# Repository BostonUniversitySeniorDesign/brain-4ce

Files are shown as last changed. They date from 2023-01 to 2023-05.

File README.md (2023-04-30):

<div style="text-align: center;">

# **Brain-4ce** - An EEG-based Brain-Computer Interface

</div>

<p align="center">
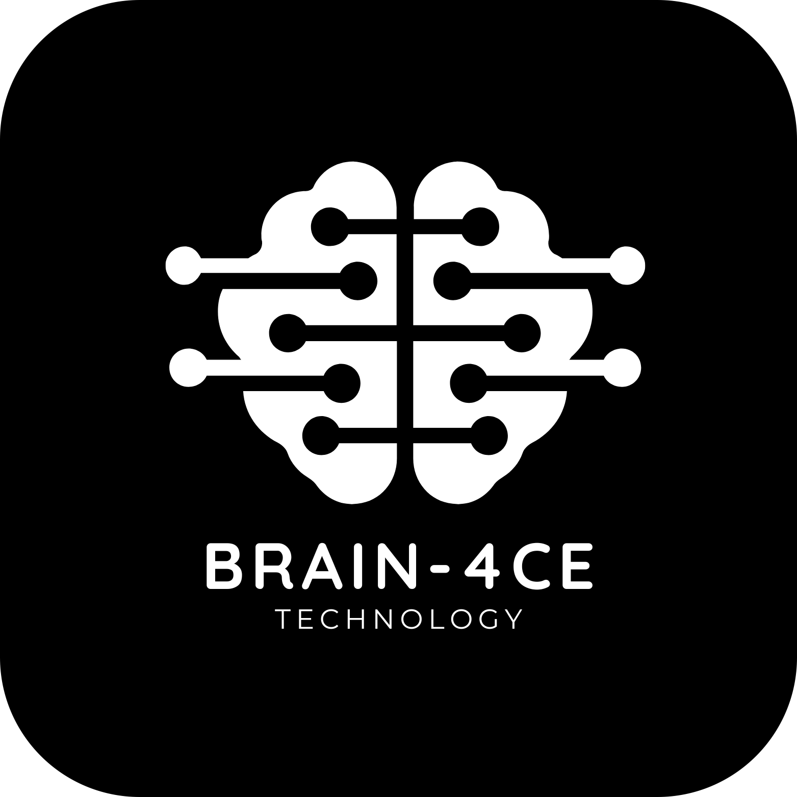
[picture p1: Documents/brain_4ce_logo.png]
Brain 4ce Logo
    
    <br>
    <em>Where thoughts become motion.</em>
</p>
<h2 style="text-decoration: underline; text-align: center">Designed by BU ECE 2023 Senior Design Capstone Team 4</h2>
<p align="center">
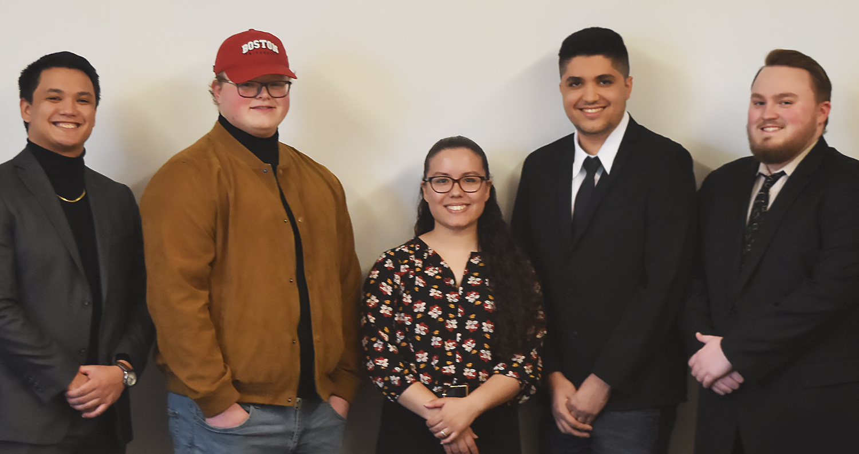
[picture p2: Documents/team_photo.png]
    
    <br>
    <em>From left to right: Brendan Shortall, Mitchell Gilmore, Dayanna De La Torres, Jonathan Mikalov, Alexander Johnson</em>
</p>
<br>

# Table of Contents
- [**Brain-4ce** - An EEG-based Brain-Computer Interface](#brain-4ce---an-eeg-based-brain-computer-interface)
- [Table of Contents](#table-of-contents)
- [Abstract](#abstract)
- [Getting Started](#getting-started)
- [Current State of the Project](#current-state-of-the-project)
- [Lessons Learned](#lessons-learned)
- [Bug Fixes](#bug-fixes)

<br>

# Abstract
The ability to manipulate objects using only your mind is no longer a far-fetched idea. While It may sound like something out of science fiction, our team has turned this into a reality. We have created a headset that utilizes electroencephalogram (EEG) technology to quickly and accurately record a user's neural activity. Our state-of-the-art deep learning algorithm then decodes these signals into predefined motor-imagery tasks.

This breakthrough technology is integrated with a computer game that provides the user with an environment to navigate using their mind. With the Brain-4ce (pronounced "Brain Force") headset, users can perform four different actions: rotating clockwise, rotating counterclockwise, moving forward, and moving backward. Each action corresponds to a physical motion that the user imagines themselves doing.

Our team was inspired to develop this project by our aspiration to bridge the digital divide for those who are physically disabled. With the Brain-4ce headset, users will be able to operate a computer, a wheelchair, and virtually anything else using nothing but their thoughts! The possibilities are endless, and we are excited to see what the future holds.
<br></br>

# Getting Started
- Please refer to our [Hardware Setup Guide](./hardware/README_HARDWARE.md) for instructions on setting up the hardware.
- Please refer to our [Software Setup Guide](./Virtual%20Environment/README_SOFTWARE.md) for instructions on setting up the software.
<br></br>

# Current State of the Project
As it currently stands, our project has three major components:
1. A working [EEG data capture headset](./hardware/electrical/cyton%20wired/) that interfaces with a [Python application](./GUI/) to monitor and record brain activity in real time.
2. A [convolutional neural network machine learning algorithm](./Physionet%20Dataloader/), trained on the recorded brain activity, for classifying motor-imagery tasks observed from a user wearing the headset.
3. [2D](./2D%20Game/) and [3D](./Virtual%20Environment/) video games developed in Python to demonstrate the efficacy of the neural network's brain activity classification.

The software communicates in real time using socket programming techniques to achieve parallelism and multithreading.
<br></br>

# Lessons Learned
- Developing on Apple Silicon, and ARM-based processors in general, is tricky for this project. Certain libraries, such as the [ChipKIT Core library](https://chipkit.net/wiki/index.php?title=ChipKIT_core) for compiling firmware onto the microcontroller, lack proper support for ARM architecture. We recommend performing all software development on an x64-based Windows machine. Some development is possible on Intel-based macOS and Linux, but it will probably save you a lot of headache to stick to Windows if possible.
- The microcontroller appears to have USB functionality built-in, which might make the USB to UART conversion unnecessary. This may be something to examine in [the documentation](https://ww1.microchip.com/downloads/en/DeviceDoc/PIC32MX1XX2XX%20283644-PIN_Datasheet_DS60001168L.pdf) during a future continuation of this project.
- The ADS1299 chip from Texas Instruments remains [difficult to obtain](https://www.findchips.com/search/ADS1299) as of Q2 2023 due to the ongoing chip shortage. We tried using the ADS1296 chip in its place, but this was unsuccessful because of differing startup and common-mode rejection configurations between the chips.
- If future boards are manufactured, it may be worth considering [paying for them to be machine-assembled](https://jlcpcb.com/parts). Assembling the boards by hand takes a long time and requires a substantial amount of electrical rules checking to ensure no shorts or incontinuity between components.
- Obtaining good skin contact for all electrodes is crucial to ensure proper reading of brain activity.
- The [OpenBCI Forum](https://openbci.com/forum/index.php?p=/discussions) is a great place to turn to for help troubleshooting. As is [their documentation](https://docs.openbci.com).
<br></br>

# Bug Fixes
- [Incorrect start byte configuration](https://github.com/atjohnson/brain-4ce-old/issues/10) - fixes an issue where the data stream is incorrectly formatted because the obsolete RFduino did some packet changing which no longer happens due to our wired USB connection.
- [Enable OpenBCI GUI to work with USB to UART controller](https://github.com/atjohnson/brain-4ce-old/issues/11) - fixes an issue where OpenBCI's GUI is unable to detect the Cyton board due to an ID mismatch with the USB to UART bridge IC.
- [Set up chipKIT Core library to work on local machine](https://github.com/atjohnson/brain-4ce-old/issues/12) - fixes an issue where Arduino IDE is unable to compile the firmware because it cannot locate the PIC32 compiler applications.
- [RXT and TXT LEDs not flashing](https://github.com/BostonUniversitySeniorDesign/brain-4ce/issues/4) - fixes an issue where the RXT and TXT LEDs on the board indicating data transmission over UART do not flash because the USB to UART bridge's firmware is configured improperly.

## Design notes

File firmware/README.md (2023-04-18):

# Firmware Configuration

OpenBCI really does not want their design to be used with a wired connection. From forum posts it is clear that their main motivation for this is safety, as a battery connection has a finite charge and a smaller discharge rate making the results of a potential hardware malfunction less dangerous. Unfortunately, the way they designed this required functionality of less popular hardware in order to transmit data, which ultimately fell into deprication. In order to make a design that is more robust to time, our team opted for a wired hardware connection. This means bypassing safe gaurds put into place that make implementation of a wired connection not possible by default.

In order to upload custom firmware to a fresh PIC32 microcontroller, the [bootloader](./UDB32-MX2-DIP.hex) must first be flashed using [MPLAB IPE](https://www.microchip.com/en-us/tools-resources/production/mplab-integrated-programming-environment) and a [PICkit 3 In-Circuit Debugger](https://www.microchip.com/en-us/development-tool/PG164130) as shown in [this video](https://youtu.be/z6AyIfWDiiU).

In terms of firmware the largest difference is the datapacket transformation done betweem the openbci cyton and the dongle. The start bit from the cyton is transmitted as `'A'` which is then converted to `0xA0` in order to be within their datapacket spec found [here](https://docs.openbci.com/Cyton/CytonDataFormat/#binary-format). In order to rectify this we edited the macro `OPENBCI_BOP` found in [OpenBCI_32bit_Library_Definitions.h](https://github.com/OpenBCI/OpenBCI_Cyton_Library/blob/master/OpenBCI_32bit_Library_Definitions.h#L19) from `'A'` to `0xA0` and made a [patch](packet.patch) in order to bypass this restriction.

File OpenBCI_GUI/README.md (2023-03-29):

# Configuring OpenBCI GUI

Since the OpenBCI GUI determines whether or not a devices is a Cyton by inspecting the vendor information on the USB controller, any device that was made with a different controller will by default not be found. To rectify this we made a patch to the OpenBCI GUI that removed the check for vendor specific indentification on the USB controller. In order to use this changes first set up an envirnment to compile the OpenBCI GUI. Details on how to do this can be found in their [wiki](https://github.com/OpenBCI/OpenBCI_GUI/wiki/Developer-Setup). After set up simply follow the commands below.

```bash
cd <This directory>
cp UART.patch <OpenBCI_GUI root directory>
cd <OpenBCI_GUI root directory>
git apply UART.patch
```

After making these changes if you follow the steps on the OpenBCI_GUI documentation to compile the project. Then the filtering that would prevent the custom design to be selectable.

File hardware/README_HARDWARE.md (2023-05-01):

# Hardware Setup
<div style="display:flex; justify-content:center;">
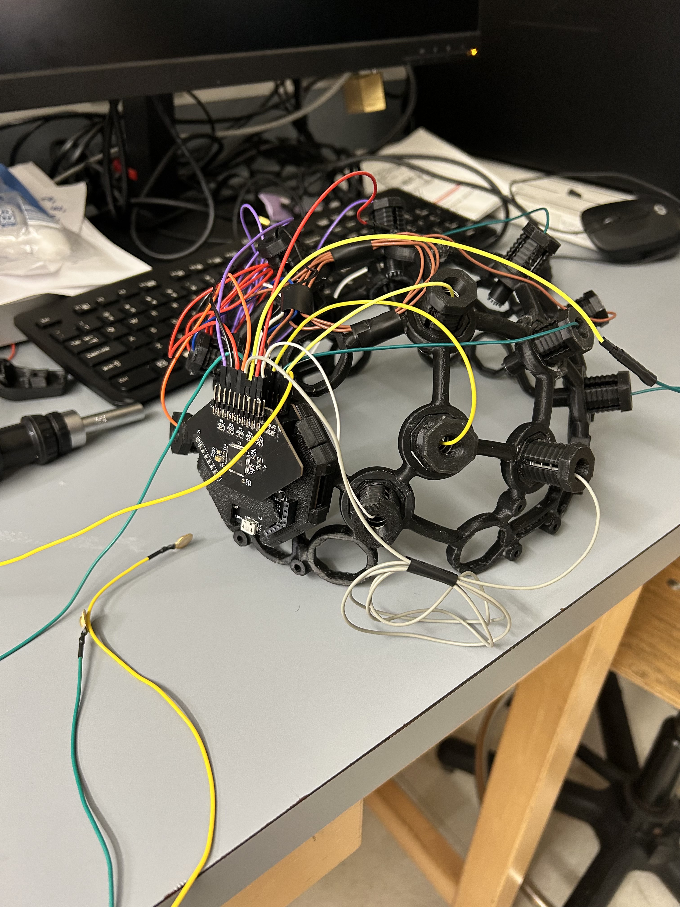
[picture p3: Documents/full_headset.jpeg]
Full Headset
  
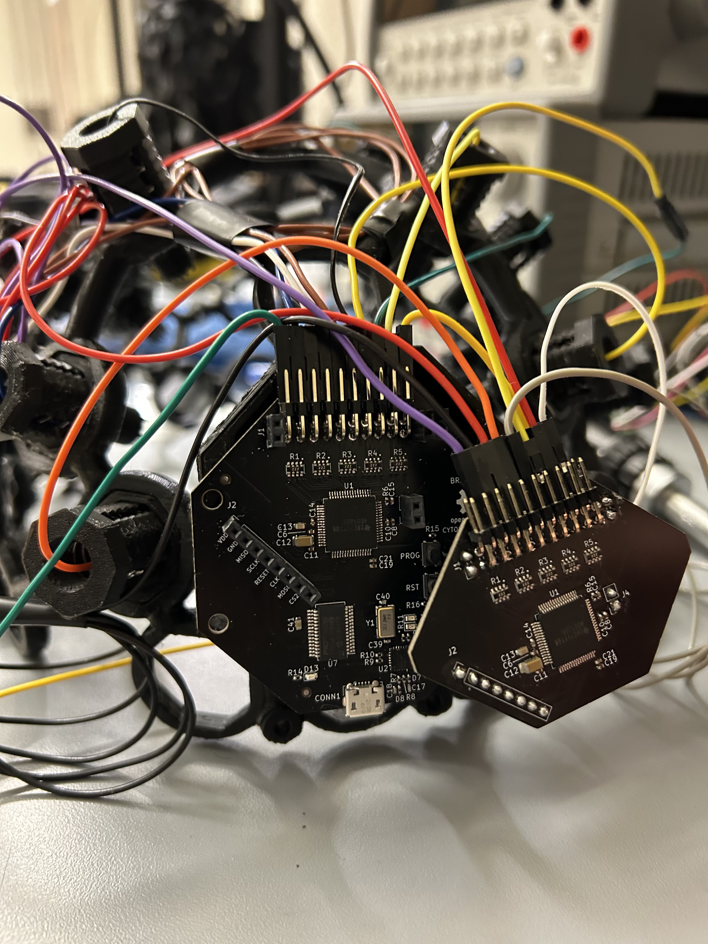
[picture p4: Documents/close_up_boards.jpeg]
Close Up of Boards
  
</div> 
<br>

The headset comes assembled out of the box with 16 electrodes placed in the rear of the headset body. The PCB is mounted in its casing on the back of the headset as well, with the probes attached to their correct pins.
1. Begin by attaching the included USB to the USB port that is visible on the Cyton board.
2. Plug the opposite end into any USB port on your PC. Ensure power is being sent to the board indicated by a blue LED on the top side of the Cyton. Once this LED is on, the hardware is ready to go.
3. If you would like to change the electrode positions, gently remove the probe by squeezing the sides of the outer electrode casing and pulling outwards. You should never change where the electrodes are connected to the boards, but if you choose to do so refer to the layout described in section 2.3.4 of the [User's Manual](../Documents/Team%204%20User's%20Manual.pdf).
4. Once you are ready to start the EEG system, connect an ear clip to each of your earlobes and place the headset on your head with the board on the back. Make sure that each of the probes is making contact with the scalp.
<div style="display:flex; justify-content:center;">
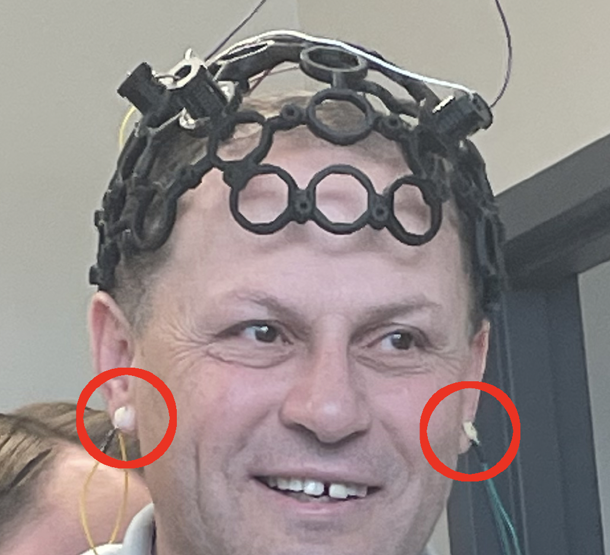
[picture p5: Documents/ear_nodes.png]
Ear Clips
  
</div> 
<br>

# Schematic/PCB/CAD Diagrams
- [Cyton Wired board schematic and PCB diagrams](./electrical/cyton%20wired/)
- [Cyton Daisy board schematic and PCB diagrams](./electrical/cyton%20daisy/)

# Bill of Materials
- [Cyton Wired BOM](./electrical/cyton%20wired/cyton%20wired%20bom.csv)
- [Cyton Daisy BOM](./electrical/cyton%20daisy/cyton%20daisy%20bom.csv)

# Significant Data Sheets
- [PIC32MX250F128B microcontroller](https://ww1.microchip.com/downloads/en/DeviceDoc/PIC32MX1XX2XX%20283644-PIN_Datasheet_DS60001168L.pdf)
- [ADS1299IPAG analog front end](https://www.ti.com/lit/ds/symlink/ads1299.pdf?HQS=dis-dk-null-digikeymode-dsf-pf-null-wwe&ts=1682901373303&ref_url=https%253A%252F%252Fwww.ti.com%252Fgeneral%252Fdocs%252Fsuppproductinfo.tsp%253FdistId%253D10%2526gotoUrl%253Dhttps%253A%252F%252Fwww.ti.com%252Flit%252Fgpn%252Fads1299)

# Power Requirements
- Micro USB to USB A power and data cable

# Vendor Information
- PCBs manufactured by [JLCPCB](https://jlcpcb.com)
- PCB surface mount components purchased from [Digi-Key](https://www.digikey.com)
- Headset components obtained from [OpenBCI](https://docs.openbci.com/AddOns/Headwear/MarkIV/?_gl=1*1e99fsi*_ga*NzI1MjAxMTkyLjE2ODI1MjkzNDM.*_ga_HVMLC0ZWWS*MTY4MjkwMDUzNC4zLjEuMTY4MjkwMDU0Ny40Ny4wLjA.)
- ADS1299 chips purchased from [AliExpress](https://www.aliexpress.us)
- PICKit 3 hardware debugger purchased from [Amazon](https://www.amazon.com)
- USB isolator purchased from [Adafruit](https://www.adafruit.com/product/2107)

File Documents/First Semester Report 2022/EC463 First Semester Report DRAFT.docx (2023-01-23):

# Boston University

# Electrical & Computer Engineering

# EC463 Senior Design Project

# First Semester Report

Submitted to

Prof. Alan Pisano

apisano@bu.edul

by

Team 04

Brain 4ce

Team Members

Alexander Johnson atjohnso@bu.edu

Brendan Shortall shortall@bu.edu

Dayanna De La Torres dayannat@bu.edu

Jonathan Mikalov jmikalov@bu.edu

Mitchell Gilmore mgilm0re@bu.edu

Submitted: 12/11/2022

#### Table of Contents

Executive Summary ii

1.0 Introduction 1

2.0 Concept Development 2

3.0 System Description 3

4.0 First Semester Progress 4

5.0 Technical Plan 5

6.0 Budget Estimate 6

7.0 Attachments 7

7.1 Appendix 1 – Engineering Requirements 7

7.2 Appendix 2 – Gantt Chart 8

7.3 Appendix 3 – Other Appendices 9

(right click on Table of Contents to update fields and page numbers automatically)

# Executive Summary - Alex

EEG-based Brain-Computer Interface

Team 04 – Brain 4ce

Individuals with physical disabilities, who struggle to operate a computer, need a noninvasive, but intuitive method of interfacing with the machine without musculoskeletal movement. We propose a wearable brain-computer interface (BCI) system to resolve this problem. Our BCI will consist of a 3D printed headset housing electrodes, a sampling board to obtain electroencephalogram (EEG) data from the electrodes, a machine learning model to classify the data into directional commands, and a 3D virtual environment to demonstrate functionality. We have designed an innovative approach to combine together the classification of neuronal action potentials (APs) with a 3D computer simulation.

(This should be written for management/public dissemination.

This will be published and distributed to ECE faculty.)

# 1.0 Introduction - Brendan

Since the turn of the century, brain-computer interfaces have grown in popularity. The number of publications surrounding this topic have nearly doubled since 2014 [1]. (https://www.frontiersin.org/articles/10.3389/fnsys.2021.578875/full) In many cases, invasive BCI technologies, which communicate with the brain via medical implant without interference from the scalp, have been shown to improve the lives of people with neurological illnesses [2]. (https://www.sciencedirect.com/science/article/pii/S0006349512033401?via%3Dihub) With this in mind, it is clear that the technology behind reading neural activity using medical implants has great potential.

However, invasive technologies may come with a slew of disastrous consequences for the user’s brain. A well documented complication of implanted neural electrodes are microglia immune responses. Microglial Cells release neurotoxins in response to pathological stimuli; neural implants have shown to amplify this response, causing major injury [3]. (https://www.sciencedirect.com/science/article/pii/S0165027005002931?via%3Dihub)

Invasive technologies for reading brain activity are also becoming increasingly more expensive. It is predicted that invasive BCIs will experience the fastest compound annual growth compared to non-invasive and semi-invasive techniques [4]. (https://www.grandviewresearch.com/industry-analysis/brain-computer-interfaces-market) The invasive approaches also include marginally higher expenses due to its physical implementation as well as required periodic medical check-ups [5]. (https://www.ncbi.nlm.nih.gov/pmc/articles/PMC3497935/) As a result, accessibility to invasive BCIs will become increasingly difficult for patients.

Our proposed solution avoids the dangerous risk of complications associated with electrode implants by implementing a safe and cost-effective method of non-invasive EEG pattern reading. As non-invasive EEG brain pattern recognition techniques improve, we hope to remove the risks associated with invasive techniques while maintaining and potentially improving the functionality of BCIs.

This project focuses on one of many potential applications of BCIs. In our use case, we hope to improve the usability of computer systems for physically disabled users, in a low-cost, low-risk way. To accomplish this, we will create a headset containing an array of EEG sensors positioned precisely around the user’s scalp. These sensors will be read by a mounted printed circuit board (PCB) that will communicate directly with a computer. As real time data is received on the computer, our machine learning algorithm will constantly analyze the data and make a prediction on the user’s intended movement. This prediction will be sent to our virtual environment, where a user-controlled object will move based on the user's intended action. This virtual environment acts as visual feedback for the user, so that they can adjust their behavior for the results they desire. This closed loop system will demonstrate the capabilities of non-invasive neural monitoring techniques, and will lay a foundation for future research involving non-invasive EEG based BCIs.

# 2.0 Concept Development - Jonathan

Here you describe your analysis of the customer’s problem and its translation into specific engineering terms. You should address:

- your engineering understanding of the customer’s problem,
- the conceptual approach you have chosen to solve the problem, and

You must reduce the customer’s needs to a small number of engineering requirements. You must identify those requirements as a 1-page attachment, Appendix 1

Elaborate on the conceptual approach for your project. Explain briefly why you chose your proposed concept, and mention one or two of the alternative solutions you considered and abandoned.

(This section should be 2-3 pages)

You MUST include a 1 page Requirements list as Appendix 1.

To address the complex challenges that neurologically and physically disabled individuals face when operating a computer, our team was immediately faced with many dilemmas regarding actual implementation. First, it was made clear that the machine learning algorithm needs to communicate with both the signal processing unit and the virtual environment efficiently. Accounting for this, we considered a variety of neural network algorithms that might work optimally given our outlying data sampling techniques as well as limited CPU memory usage. These were including but not limited to: Deep Recurrent Neural Networks (DRNNs), Hidden Markov techniques, as well as the Bidirectional Long-Term Short Memory Neural Network (LSTM). After careful review of the benefits of each deep learning method, it was concluded that the LSTM model would be the best fit for our data classification model given its lack of over-reaching memory usage as well as its consistent learning ability to classify motor imagery tasks. Classifying motor imagery tasks is very important for overlying project concept as they deal directly with the backbone of an EEG-based brain computer interface. As such, we anticipate that our model needs to classify data accurately for it to be optimally used by a disabled individual.

Another core tenet behind a brain-computer interface is its ability to be worn with comfort and ease-of-access. Thus, it must not cause too much pressure to the forehead of the individual and must not be congested with wires across their desk or table. Understanding that some disabled individuals may tend to feel more sensitive pressure to the head, our team has agreed upon a thorough weight requirement of no more than 1 kilogram. This includes the headset in its entirety as well as all its connected cables to the Arduino Uno and CPU. To account for the lightweight requirement, we implemented an OpenBCI© 3D print design that allowed us to construct a headset ¼ of our weight requirement (excluding all required cables).

Our hardware requirements, which were initially relatively straightforward to design, ended up being presented with creative challenges. In one specific example, the printed circuit board’s Bluetooth module (important as it serves a direct link between the MCU and CPU), was no longer being sold in stores and had become essentially defunct. As a result, our team had to develop a new set of engineering requirements that maintained our design’s level of efficiency while also establishing an efficient method to connect a circuit board to a CPU. As a result, we developed an Arduino Uno component for the underlying architecture that will serve an important role in transferring real-time signal processing data into our CPU, to be received by the machine learning algorithm. This component of our project also needs to be optimally efficient, in such a way that it can at least process up to 500 samples of alpha & beta brainwave data per millisecond. For the detection of specific motor imagery tasks present within an EEG, our team discovered a variety of data features that can be used to relatively classify the thought being present. As a particular example, the P300 wave, which is commonly used by lie-detectors as well as other BCIs, can be seen in an EEG as a physiological pattern being produced by the thought of a particular reaction (ie. decision making).

The virtual environment component of the project, while primarily serving as a proof-of-concept for the core brain-computer interface, serves an integral role in displaying the role of BCIs used in everyday life. As such, the environment itself was designed to be graphically oriented to be appealing to a wide array of users, and present only simple features. If anything more be present, epilepsy patients or others with visual sensitivity will not be able to use this component to their advantage. An important engineering requirement regarding the use of the virtual environment is its frame rate, graphics support, and its ability to process machine learning classification in real-time. The reason of its importance mostly stems from the ability that disabled individuals need to be able to operate in a timely manner so as to not inconvenience them compared to other products on the market. As such, we discovered that the graphics library used for our 3D environment (Panda3D) not only supports an adequate framerate (usually up to 60 frames per second) but also supports a wide array of graphics cards, ranging from various versions of NVIDIA to Intel.

# 3.0 System Description - Alex

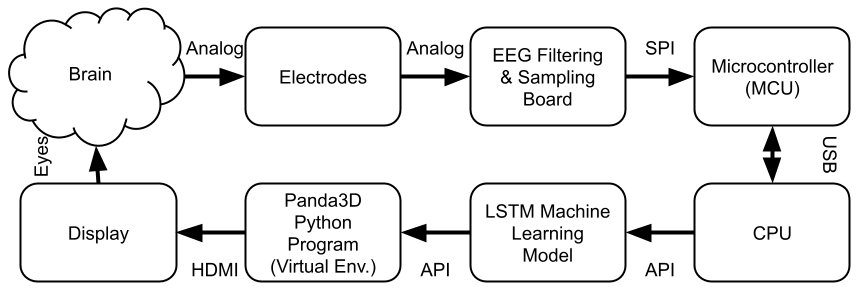
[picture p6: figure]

Figure 1. Block diagram of the system.

Our system begins with a set of reusable dry EEG electrodes housed in OpenBCI’s Ultracortex Mark IV headset, 3D printed using PLA material. These electrodes, located on the user’s scalp following the international 10–20 system configuration, read analog motor-imagery electrical signals in real time from the user’s brain and pass those signals along wires to OpenBCI’s Cyton PCB. Those analog signals are then filtered, digitally sampled, and passed along the PCB in 8 channels to the microcontroller. The microcontroller processes the digital signal into usable data for transmission over USB.

After the data is transmitted over USB, the computer decodes the input using the OpenBCI software suite, and it is then fed through our long-short term memory (LSTM) artificial neural network by a custom designed API. The LSTM model then classifies the data into 4 classes each representing different directions: left, right, up and down. This new dataset is interpreted by another custom API to generate the corresponding object movement in our virtual environment Python application. The final visual output of our virtual environment is displayed on a computer monitor using an HDMI connection. The user then sees this movement on the computer screen and can adjust their motor-imagery task thought patterns accordingly.

The user interface is a three-dimensional virtual environment generated in Python using Panda3D libraries. It consists of an object, tentatively a sphere, suspended on a flat surface in the environment. A set of obstacles move towards the sphere, and the user is tasked with moving the sphere out of the way before it collides with the obstacle. This game design is how our proof of concept is demonstrated.

Here you describe in technical detail WHAT YOU WILL PROVIDE as a solution. It should be as detailed, specific, quantitative, and engineering-oriented as possible.

Avoid grand promises and vague descriptions. Ruthlessly edit collective, vague adjectives and claims (e.g. “We will have high power and long life in our nuclear transmitter”). Follow the concept you are recommending from section 2.

You MUST include a system block diagram (approximately a level 2 functional decomposition) for your system/software, including a brief narrative explanation. The system block diagram should identify clearly the major subsystem blocks. Directed arrows should represent data or control flows. It is appropriate to use a full page for the system block diagram, and to import a figure developed in another application, e.g. Visio.) The following was done in Word Draw.

Figure 2. Block diagram of the Beam Transporter.

If appropriate, include a discussion of the user interface with your preliminary GUI. You can sketch the project or include a photo of your mockup.

If it is a software project, you should include high-level pseudocode of how the project will operate.

(This section should be 2-3 pages. It is an overview description.)

# 4.0 First Semester Progress - Dayanna

4.0.1 Hardware Progress

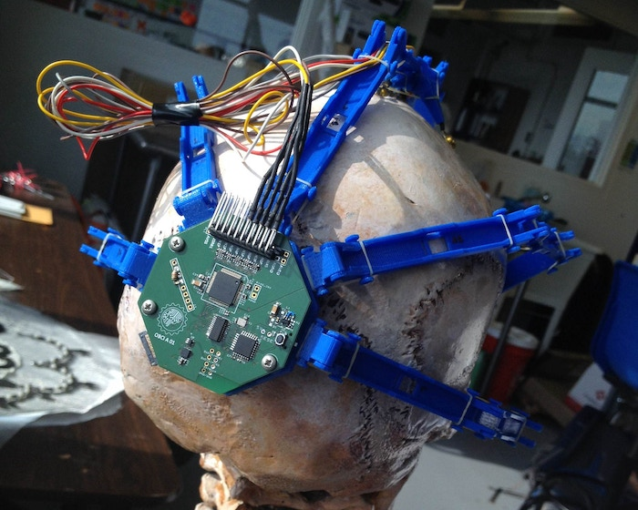
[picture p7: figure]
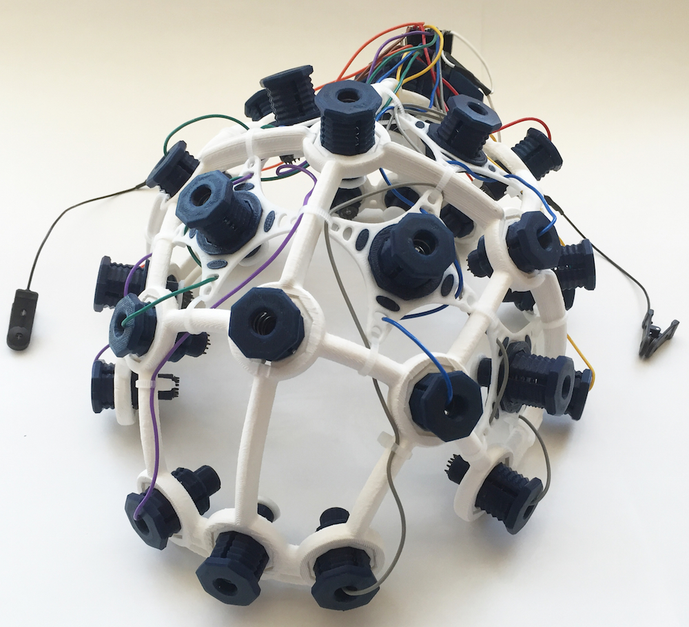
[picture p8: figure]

Figure 2a Figure 2b

Figure 2: The headset Design. Figure 2a depicts the original design. Figure 2b depicts the new updated design.

4.0.1.1 Headset Design and Fabrication

We based our headset on open source designs we were able to find. After 3D-printing the first iteration (figure 2a), it was promptly discarded due to structural integrity concerns. Specifically, the fact that it was held together with orthodontic elastics. We have now moved onto the second iteration of the headset (figure 2b) which we deem to be more structurally intact and solid. Moreover, it has better assigned locations for the electrodes. Together, this makes the design not only structurally better but also more comfortable for the user.

4.0.1.2 Circuit Board Design and Fabrication

We are modeling our circuit board after the OpenBCI sampling board. Due too the cost of the board being around $1000, we are creating it in-house. This semester we printed the PCB, ordered the necessary components, and are beginning the process of soldering said components onto the board. We have run into one component issue which is with the Bluetooth/RF module. The module used on the original OpenBCI board has been discontinued and is no longer on the market. Handling this situation and researching alternatives was a top priority for this semester in order to finish the board and begin collecting data samples.

4.0.1.3 Collecting EEG data

This semester we created our first prototype of the EEG system where our goal was just to receive some electrical output from the system (no emphasis on collection yet). To obtain proper readings from the EEG electrodes, we had to amplify our voltage output by 900x. To amplify the voltage output, we created a differential amplifier circuit using a set of resistors, a 5V power supply, and an MCP6002 operational amplifier. As an additional setup, electrode wires were connected to the voltage output of the circuit in order to obtain a potential physiological response from a test subject. In order to test the performance of the EEG electrodes, we attached them to multiple test subjects’ arm using conductive paste. Additionally, we detached them from the arm and placed them directly on the forehead to examine a potential change in results. Ultimately, we were unable to obtain readings from the EEG electrodes. The oscilloscope displayed a constant zero voltage regardless of the electrode placement on our test subjects. Moving forward, the electric circuit needs to be changed to address these issues.

As a side attempt to collect data, research was done into Arduino-based EEGs. While it may not be as precise, we are hoping that it will provide usable data that can then be used to train the LSTM neural network. The parts have been ordered and we have begun 3D printing the necessary components to create this smaller system.

4.0.2 Software Progress

4.0.2.1 Machine Learning Model

We have begun working on an LSTM algorithm; however, it has not yet been trained nor tested on our data due to the inability to successfully collect any to this point. The purpose of working on one thus far has been to familiarize ourselves with inputting and reformatting data into LSTMs, working with LSTM neural networks

To this date, the LSTM neural network has been trained and tested on online public databases containing EEG data. In some cases, this has failed due to a lack of understanding of the data. Machine learning algorithms are sensitive to matrix dimensions and being unfamiliar with them, and what each row/column may signify poses a problem. The NN has worked on some EEG data, namely if it is picking up readings of physical activity. This however, is different from trying to pick up thoughts which is our ultimate goal.

The most successful tests run thus far have been on physical motion. Specifically, the data that uses an accelerometer or some other type of sensor readings to measure motion/ type of motion. This has worked with over 90% success.

4.0.2.2 Virtual Environment

This semester we have started setting up Blender for our final virtual environment. The first task completed was running Panda3D, a game engine used to render 3D environments/games, to test for graphic issues and framerate compatibility. We did this by running sample files provided by the library and measured a variety of statistics (FPS, refresh rate, render distance) and compared them on different operating systems, specifically Windows and MacOS.

We created a draft Blender virtual environment for the initial prototyping and construction of the virtual game. This was followed up by interfacing Blender models with a Panda3D script, as this will be used to control the game in real time.

This section is a detailed summary of the progress your team has made this semester. Include key results from your First Deliverable Testing.

# 5.0 Technical Plan - Mitchell

The first stage in completing our solution is EEG assembly. We have components ordered and currently in shipping but following the arrival we will have the following parallel tasks.

- Task 1: Assemble EEG PCB
  - Description:

The EEG PCB shall be assembled using already purchased components. It shall be assembled in accordance with the Schematic and Layout save for a few divergent cases documented in the logbooks. Additionally This will entail writing the provided firmware from OpenBCI to the onboard microcontroller.

  - Lead: Mitchell
  - Support: Brendan
- Task 2: Assemble EEG Headset
  - Description:

The EEG headset shall be assembled in accordance with the assembly instructions provided by OpenBCI in the UltraCortex repository (https://github.com/OpenBCI/Ultracortex/tree/master/Mark_III_Nova).

  - Lead: Brendan
  - Support: Mitchell

Following completion of these tasks we will begin our second stage focused on data collection to train the machine learning model.

- Task 1: Collect Data from EEG
  - Description:

Data shall be collected from our prototype EEG for ML training purposes using OpenBCI GUI. The data collection process will be automated by an instructional video that will guide a user through different visualization and movement tasks to be classified.

  - Lead: Mitchell
  - Support: Brendan
- Task 2: Label EEG Data
  - Description:

Using the timing intervals of the guided video we shall assign labels to certain sections of the EEG so the ML algorithm can be trained in a supervised manner.

  - Lead: Brendan
  - Support: Mitchell
- Task 3: Forward Data to ML Lead
  - Description:

Following labeling the dataset will be released to the ML lead to begin training the ML algorithm on modality specific data.

  - Lead: Mitchell
  - Support: Brendan

After data collection we will begin the EEG redesign and ML design, train, and test phases as well as complete the virtual environment.

- Task 1: Schematic Redesign
  - Description:

The original design for the PCB is inherited from a previous open source project that is no longer maintained. In its base state it does not meet our needs, so we shall redesign it to transition from obsolete wireless communications to usb for sending data to the computer, while doubling the number of probes and removing unwanted components.

  - Lead: Mitchell
  - Support: Brendan
- Task 2: EEG Layout
  - Description:

Following the schematic redesign to include all the features we need. We shall layout a PCB in accordance with the new schematic so our new electrical system can be fabricated.

  - Lead: Mitchell
  - Support: Brendan
- Task 3: Design and Train ML Algorithm
  - Description:

Following the creation and labeling of data we shall begin work creating a LSTM Neural Network that will be trained to classify the different observable action potentials (AP) in the brain corresponding to different premotion thoughts.

  - Lead: Dayanna
  - Support: Brendan, Mitchell
- Task 4: Test ML Algorithm
  - Description:

Following training and hyperparameter tuning a partition of the dataset not yet seen by our machine learning model will be used to quantify real world performance.

  - Lead: Dayanna
  - Support: Brendan, Mitchell
- Task 5: Develop Signal Processing Scheme
  - Description:

EEG signals are inherently very noisy so as to mitigate errors associated with noise, various processing techniques will be tested in an attempt to improve classification. These methods are but not limited to cepstral analysis, parametric signal modeling, Kalman filtering as well as other to be determined relevant methods of deconvolution and reconstruction.

  - Lead: Mitchell
  - Support: Brendan, Dayanna
- Task 6: Finalize Virtual Environment
  - Description:

In order to show visually our system functioning we need a virtual environment that has an object that can be controlled with user input. Eventually this user input will be replaced by the ML predictions, but in order to finalize the virtual environment separately from the rest of the project it shall initially be configured to take in a mouse and keyboard as input.

  - Lead: Jonathan
  - Support: Alex

Following completion of the redesign phase we will need to fabricate and assemble the new EEG PCB.

- Task 1: Fabricate PCB
  - Description:

After the PCB is layed out, it will need to be fabricated. Due to the stackup of the design, we will not be capable of fabricating the PCB at BU. Therefore, the design will need to be fabricated externally through a third party vendor.

  - Lead: Mitchell
  - Support: Brendan
- Task 2: Assemble PCB
  - Description:

Following PCB fabrication the boards shall be assembled to have all its components soldered to the board to achieve full functionality and so the on board microcontroller unit (MCU) can be programmed. We will explore options for external assembly to streamline the design or assembling internal at BU.

  - Lead: Mitchell
  - Support: Brendan

After having the redesigned EEG made physically it will be time to integrate all the separately developed components into a pipelined system.

- Task 1: Interface ML Algorithm with EEG in realtime
  - Description:

With the ML Algorithm and the EEG machine tested and verified as standalone units, the two shall then be integrated together into a pipelined system.

  - Lead: Dayanna, Alex
  - Support: Brendan, Mitchell
- Task 2: Interface between ML ALgorithm and Virtual environment in real time
  - Description:

With the ML algorithm and virtual environment tested and verified as standalone units, the two shall then be integrated together into a pipelined system.

  - Lead: Dayanna, Jonathan
  - Support: Alex

Following the completion of these tasks we will have a fully functional end-to-end system to read EEG pre-motion thoughts into observable computer actions.

Describe how you plan to complete your proposed solution.

The performance period of this plan is December 11, 2012 – May 1, 2013. You should not discuss tasks that are already completed or plans that are in the past! Remember the functional testing of your project is the week of April 1 (This is when the project is “due”)

Organize this section as a discussion of tasks and milestones, integrated with your professionally prepared Gantt Chart (Appendix 2)

Tasks should be clearly named. They should be described with a verb-an action word. They should have a clear, measurable deliverable product at their completion.

Task 2. Battery power supply

A 3V, 200 mA battery power supply shall be designed, fabricated and tested. It shall be rechargeable from an external connector and meet specifications for weight, battery life, and heat dissipation. The design should be tested with a dummy load of 900 ohms. Lead: Captain Kirk; Assisting: Scottie.

(No more than 4 pages.)

# 6.0 Budget Estimate - Brendan

Figure 3: The team’s current expenditures, and a summary of our remaining budget.

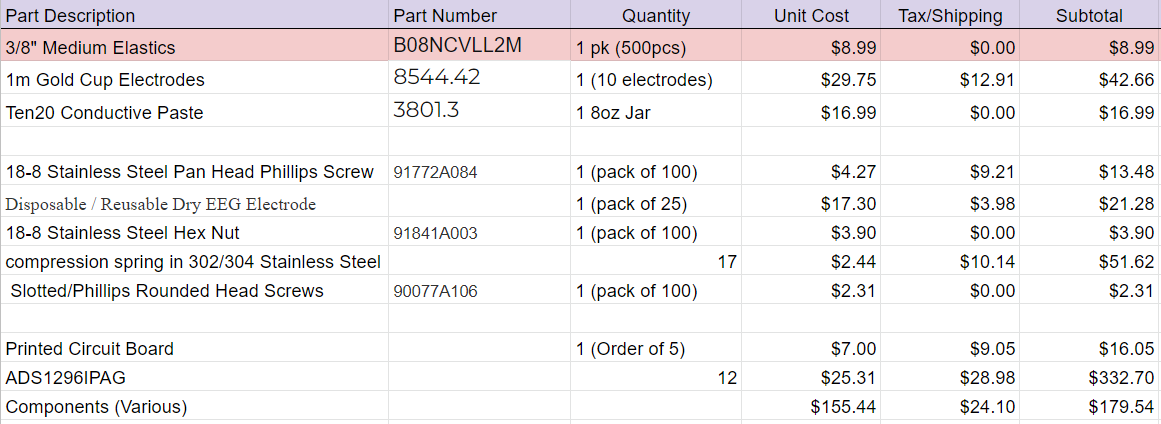
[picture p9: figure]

Our budget is limited to $1,000 from the Boston University ECE department. However, we have received additional funding from the Arrow Electronics Innovation Fund in the amount of $2,500. Our team plans to stay within the original $1,000 budget, but the additional funding gives us a safety cushion if need be.

With a large portion of our project being strictly software, our budget is almost exclusively used on hardware. This includes the physical headset itself, the EEG sensors, and the PCB. The first 8 items in our materials list refer to the headset. These items include electrodes, screws and bolts, springs and other various hardware needed to construct our 3D printed headset. The last three items involve the PCB and the necessary components. The part listed as “ADS1296IPAG” refers to a bio-sampling chip that will be integrated into the circuit board. The minimum quantity to order was 12. We needed only 4 or so total, but this part is essential to our project and there are no other viable alternatives. We decided buying 12 and spending the additional money is in the team’s best interest. Lastly, the item listed as various components refers to diodes, capacitors, resistors and whatever other small electronics we need for the circuit. A more detailed list of these components can be found in the appendix section 7.3.1.

In all, we have spent roughly ⅔ of our allocated budget. With that being said, essentially all of our necessary purchases have been made with no major foreseeable expenses . Financially, we are in a very comfortable position; However, we will continue to track our expenses and ensure that we remain within budget.

# 7.0 Attachments

# 7.1 Appendix 1 – Engineering Requirements

Team # Team Name:

Project Name:

Requirement | Value, range, tolerance, units
Headset circumference | <=
Power | 1GJ photon source, and 3V battery
Transport range | >100 light years
Transport nodes | 3 in simplex mode (no return possible); 2 in duplex mode (round trip stored)
Radiation dose | 20 REM/trip +1 REM, -3 REM
Transport error rate | < 10⁻¹¹ molecules of normal body mass < 10⁻¹⁵ molecules when sending DNA data

These are your requirements specifications that transform the customer’s needs and wants into specific engineering requirements. See the course textbook regarding the formation of appropriate specifications. Generally these are at the system integration level. Each unit that you design will have its own internal specifications, but these are usually not listed in a proposal.

Specifications should not include vague environmental constraints.

Specifications should not be statements of technology preferences or early design decisions (e.g. “The unit shall use Li ion batteries” is not a specification.)

Not more than one page.

# 7.2 Appendix 2 – Gantt Chart

Here you provide a STANDARD PRESENTATION OF THE TASKS, MANAGEMENT, AND SCHEDULE of your efforts. You can access MS Project to create a professional Gantt Chart and cut and paste the chart here. (This template was done MS Project and saved to Word. Remember: Clear date headers; dependencies; milestones; hierarchical tasks; course milestones.

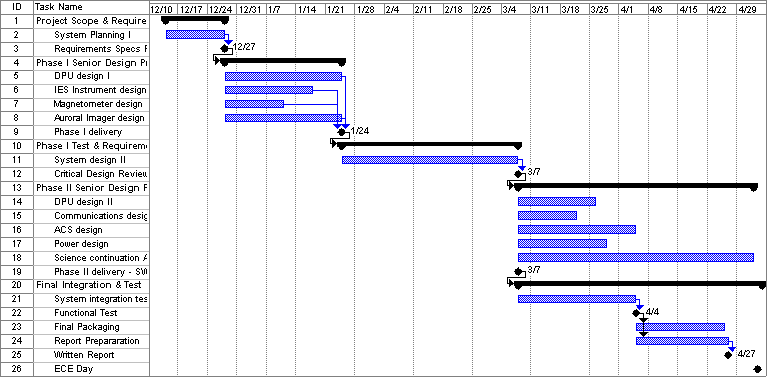
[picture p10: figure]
PjCopyPic

You need not include other MS Project columns like start and end dates, durations, support, etc. Make major milestones clear.

# 7.3 Appendix 3 – Other Appendices

Other typical attachments that are added to bolster the competitiveness of your proposal:

- Technical references (in proper bibliographic form) including key URLs.
- Your drawings and schematics (rather than embedding in text)
- Team information sheet (Biographical paragraph on each member; phone numbers and e-mail, history of team and company)

Do not pad with mundane data sheets and application notes.

7.3.1

A more detailed list of the individual components listed in Figure 2.

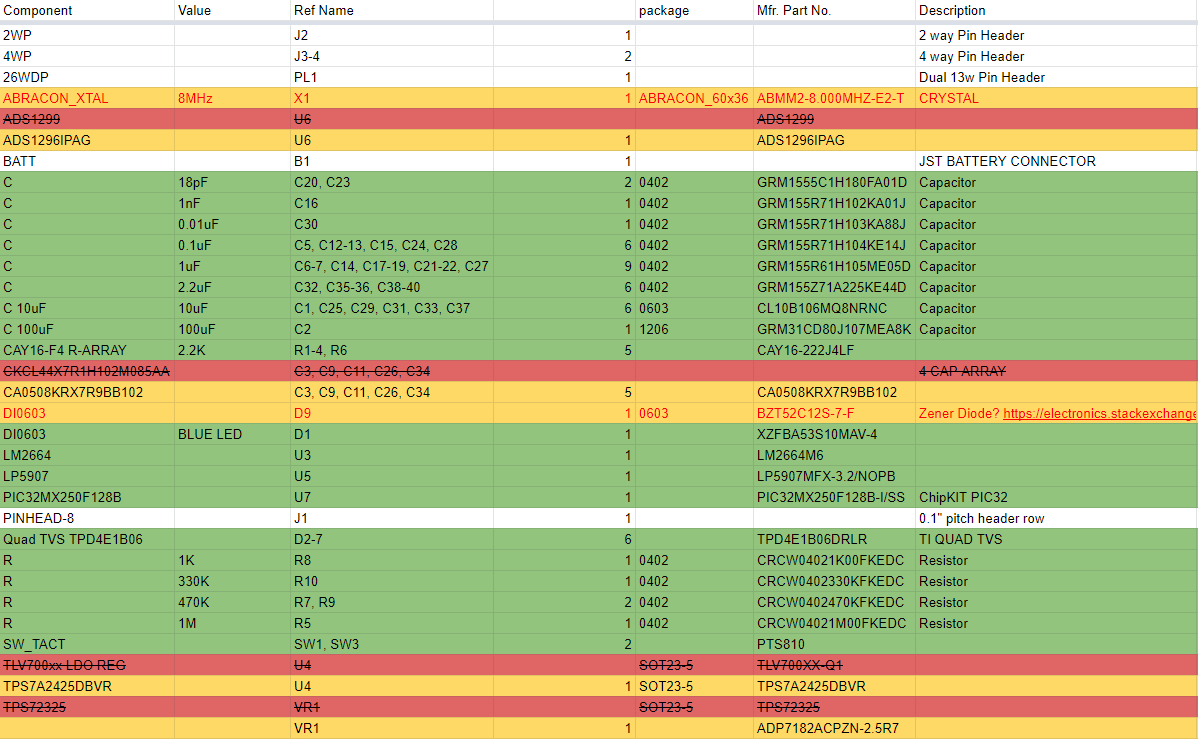
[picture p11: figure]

References:

[1] S. Saha et al., “Progress in Brain Computer Interface:

Challenges and Opportunities,” Frontiers in Systems

Neuroscience, vol. 15, Feb. 2021, doi:

10.3389/fnsys.2021.578875.

[2] L. R. Hochberg, “Intracortical Brain-Computer Interfaces for the

Restoration of Communication and Mobility,” Biophysical Journal,

vol. 104, no. 2, p. 376a, Jan. 2013, doi: 10.1016/j.bpj.2012.11.2094.

[3] V. S. Polikov, P. A. Tresco, and W. M. Reichert, “Response of

brain tissue to chronically implanted neural electrodes,” Journal of

Neuroscience Methods, vol. 148, no. 1, pp. 1–18, Oct. 2005, doi:

10.1016/j.jneumeth.2005.08.015.

[4] “Brain Computer Interface Market Size | Industry Report,

2027,” Available:www.grandviewresearch.com.

https://www.grandviewresearch.com/industry-analysis/brain-

computer-interfaces-market

[5] J. Shih, D. J. Krusienski, and J. R. Wolpaw, “Brain-

Computer Interfaces in Medicine,” Mayo Clinic Proceedings,

vol. 87, no. 3, pp. 268–279, Mar. 2012, doi:

Spell Check Everything!!!!

Paginate and edit footers and headers for your team.

Work through at least two drafts before submitting final document.

DO NOT bind, put in fancy covers or otherwise embellish. Simply clip with spring binder in upper left corner.

Use MS Word or PDF format for final document.

Submit one soft copy to course via Blackboard Digital Drop Box, and one copy to customer (include cover letter to customer).

The body of the proposal should not exceed 20 pages.

(This excludes the cover page, table of contents, executive summary, and attachments.)

Team X YourTeamName 11/15/16

Team X YourTeamName

EC 463 – BOSTON UNIVERSITY ELECTRICAL & COMPUTER ENGINEERING CAPSTONE SENIOR DESIGN PROJECT

Project Proposal page

Project Proposal

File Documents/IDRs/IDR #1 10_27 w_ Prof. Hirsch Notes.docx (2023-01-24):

- We need low noise instrumentation amplifiers
- Maybe directly solder parts on a PCB
- Breadboard is worth a try
- Compare price vs accuracy
- Avoid long traces and wires to improve performance (reduces noise)
- Vladimir Kleptsyn room 106 near senior design rooms for chips
- Maybe Dayanna can get wholesale stuff for us from CVS

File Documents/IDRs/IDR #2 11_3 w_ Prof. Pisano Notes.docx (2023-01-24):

- What can we show them in 2 weeks?
  - What can we put together that shows a viable test case
  - Shoot for hardware prototype
  - Signal generator and have it display it might be a viable first prototype
  - Likes the fact that we’ve looked at a lot of stuff
  - Thinks this is a great project and is very excited to see this come to fruition

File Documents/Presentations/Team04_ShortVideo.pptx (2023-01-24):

## Brain Force An EEG-Based Brain-Computer Interface

By Alexander Johnson, Brendan Shortall, Dayanna De La Torres, Jonathan Mikalov, Mitchell Gilmore
Client: Alan Pisano
Team 04

## Project Goal

To use a brain computer interface to aid disabled individuals in using a computer by reading neural activity related to thoughts of motion and translating these thoughts into distinct commands.

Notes: “Tweetable” summary of your project - 30 seconds or less

## System Requirements & Components

01

3D Printed Headset

- Comfortable, easily removable, dry EEG sensors.
- Lightweight, feasible to wear for long periods of time.
- Structural integrity will hold over multiple uses.

- Biosampling, Filters.
- 12+ Channels
- USB Connectivity

02

EEG Sampling Board

03

Machine Learning Model

- LSTM Neural Network
- 4+ classifiable states
- 60+% accuracy

04

Virtual 3D Environment

- Translate ML output into distinct actions.
- Small tasks for users to complete.
- Make a scoreboard for ECE day competition.

## Usability of Product

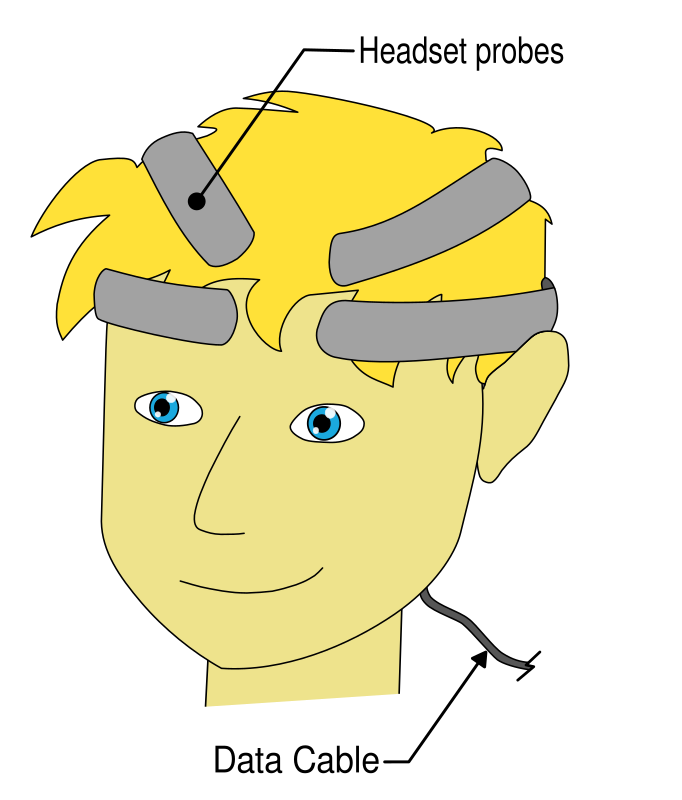
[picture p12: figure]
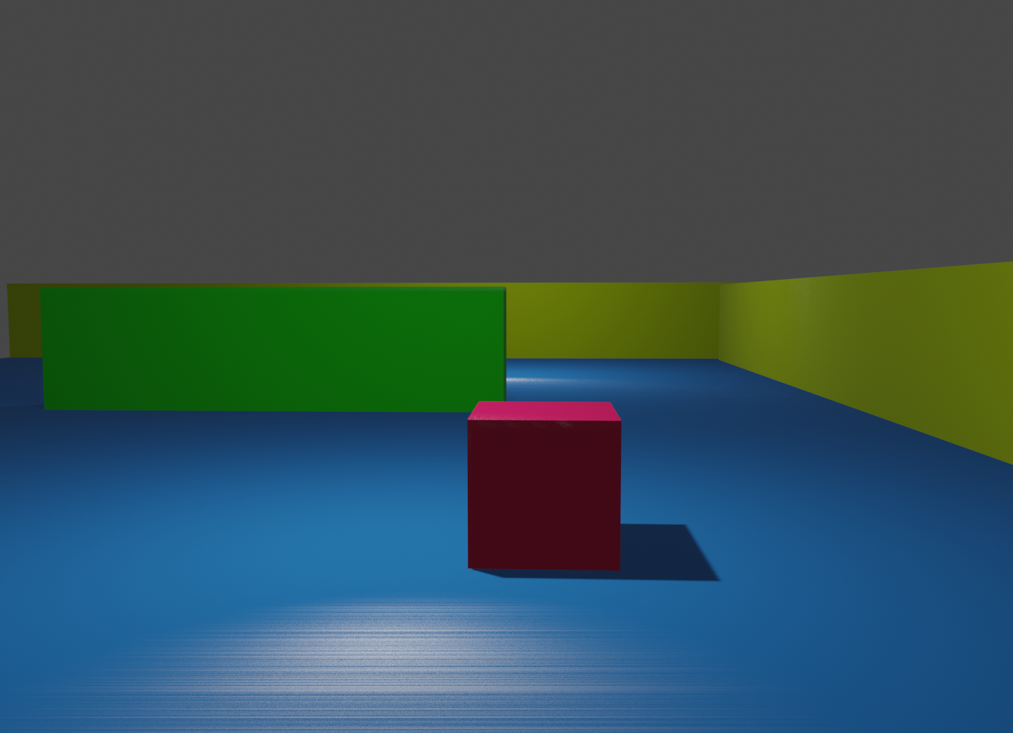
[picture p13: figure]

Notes: How would someone use your project? This is a non-technical, and functional overview of usability.

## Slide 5

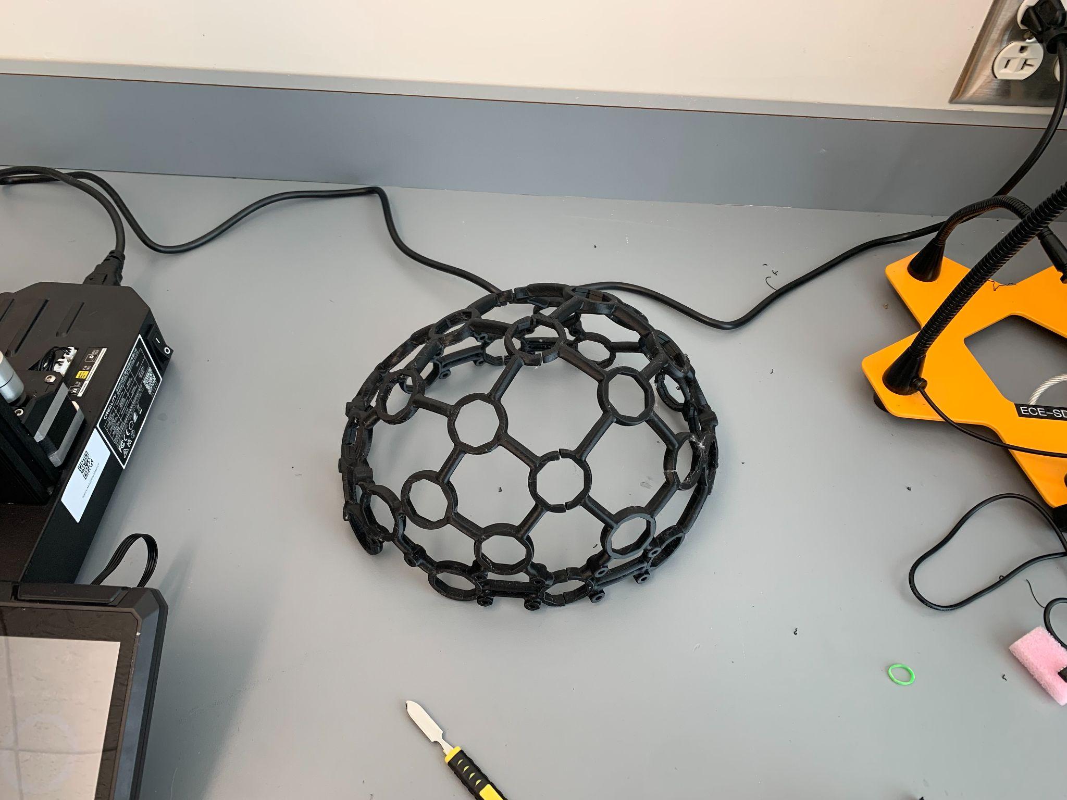
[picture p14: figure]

## Initial Prototype Test

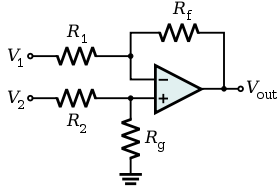
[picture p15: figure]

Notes: “Tweetable” summary of your project - 30 seconds or less

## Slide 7

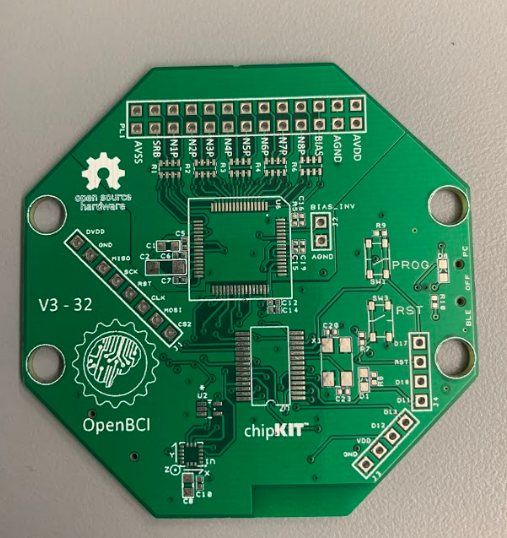
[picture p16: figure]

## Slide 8

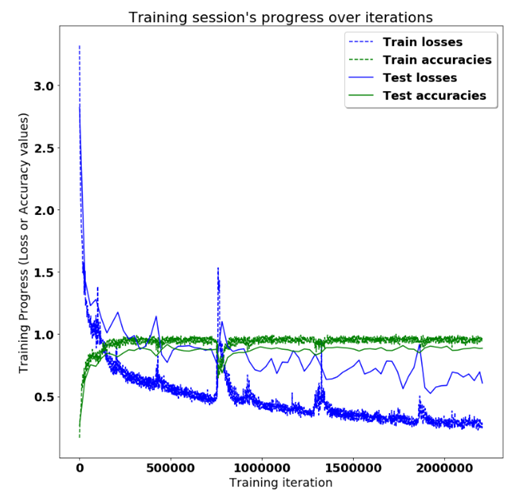
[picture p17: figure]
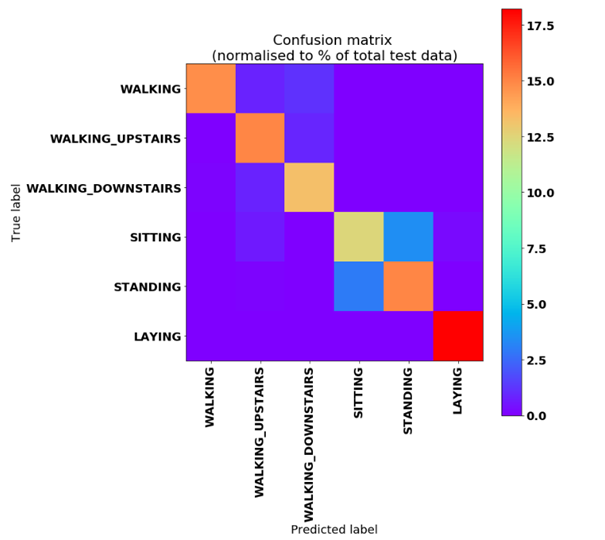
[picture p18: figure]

## Last Stage/ Working Product

Fully integrate the headset, neural network, and virtual environment to function seamlessly in real time.

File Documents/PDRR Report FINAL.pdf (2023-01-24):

EC 463 – BOSTON UNIVERSITY ELECTRICAL & COMPUTER ENGINEERING CAPSTONE SENIOR DESIGN PROJECT | 1

# Boston University Electrical & Computer Engineering

## EC463 Capstone Senior Design Project

# Problem Definition and Requirements Review

EEG-based Brain-Computer Interface

Submitted to:

Prof. Alan Pisano
apisano@bu.edu

by
Team 04
EEG-based BCI
Team Members:

Alexander Johnson atjohnso@bu.edu Brendan Shortall shortall@bu.edu Dayanna De La Torres dayannat@bu.edu Jonathan Mikalov jmikalov@bu.edu Mitchell Gilmore mgilm0re@bu.edu

### Submitted: 10/14/2022

## Customer Sign-Off _______________________________________

EC 463 – BOSTON UNIVERSITY ELECTRICAL & COMPUTER ENGINEERING CAPSTONE SENIOR DESIGN PROJECT | 2

# EEG-Based Controller for Navigating a Virtual 3D Space

### Alexander Johnson, Brendan Shortall, Dayanna De La Torres, Jonathan Mikalov, and Mitchell Gilmore, Team 04

Abstract—This project demonstrates the capabilities of non-invasive electroencephalograms (EEGs) in predicting an
intended movement of a user. A wearable headset containing an array of sensors relays neural information to a signal
processing unit, which transforms the raw input into data more suitable for further processing. From there, a trained machine learning algorithm determines a user’s intended action in a virtual 3D space. This grants the user three degrees of freedom. The intended actions will be displayed on a screen depicted as an object moving through a videogame-like three-dimensional space. This will provide feedback to the user and allow them to make adjustments. The user will be given a task to complete within the virtual environment to demonstrate the effectiveness of the device.

Index Terms—algorithm design and analysis, machine learning, signal processing, virtual environment modeling
—————————— ◆ ——————————

### 1. NEED FOR THIS PROJECT

Since the dawn of the 21st century, brain-computer
interfaces have drastically grown in popularity. Publications surrounding the topic of brain-computer interfaces (BCIs) have nearly doubled in size since 2014 [1]. In many cases, invasive BCI technologies, which communicate with the brain without interference via medical implant, have been reported to improve the lives of people with neurological illnesses [2]. With this implication in mind, the technology behind reading neural activity has incredible potential.
However, invasive technologies may come with an onslaught of arguably disastrous consequences for the human brain. One particular result of an implanted neural electrode is an unanticipated microglia immune response. Microglial Cells release neurotoxins in response to pathological stimuli; neural implants may inadvertently amplify this response, causing major injury [3].
Invasive methodologies of reading brain activity are also becoming increasingly more expensive. It is predicted that invasive BCIs will experience the fastest compound annual growth rate compared to non-invasive and partially invasive techniques [4]. The invasive approach also includes hefty expenses for its physical implementation as well as periodic medical checkups [5]. As a result, invasive BCIs used for

curing neurological-related illnesses will only be more difficult for patients to obtain.
Our solution to avoid encountering the dangerous risks and burdens of electrode implants by implementing a safe and cost-effective method of non-invasive electroencephalogram (EEG) pattern reading. It is hoped that invasive methods of measuring brain activity may dwindle as more noninvasive EEG brain pattern recognition techniques become further improved.

### 2. PROBLEM STATEMENT AND DELIVERABLES

### 2.1 Problem Statement

The non-invasive approach of reading brain activity derives from a common methodology used among researchers studying brain-computer interfaces (see “Competing Technologies”). This method involves the user wearing a relatively compact and lightweight headset with electrodes attached to read signals from the user’s brain activity.
An external signal processing unit will be connected to the headset using a wire. Within this unit, signals will be read consistently from the headset. Then, the data read from the brain will be automatically transferred to a computer also connected via wire.
The computer will serve a significant level of importance throughout the making of this project. While the computer is on, a machine learning model will be running in order to appropriately classify the user’s choice of action. Once a choice of action is classified, a virtual simulation will account for the user’s decision in real-time. This simulation will contain a 3D object

EC 463 – BOSTON UNIVERSITY ELECTRICAL & COMPUTER ENGINEERING CAPSTONE SENIOR DESIGN PROJECT | 3

controlled by the user via brain activity; the object
will move in a specific direction depending on the
user’s course of action.

### 2.2 Deliverables

For this project, we will be dividing the work into three main priorities. Each respective component will serve an essential role in meeting our objectives. They are the following:
1. A cost-effective, non-invasive EEG headset capable of taking accurate measurements of electrical activity in the brain will be created. It should do so without an excess of diodes and glue placed on the head. The time to set up and use the product should be as quick and painless as possible.
2. A simple 3D virtual space comprised of 1) an open field with enough space to test out the full scope of user maneuverability, and
2) an obstacle course field for the user to maneuver the object through in a controlled environment.
3. A machine learning algorithm capable of processing the EEG signals with minimal delay. The algorithm should be capable of translating those signals into up, down,
left, | and | right | movements | and
counterclockwise and clockwise rotation commands that navigate the object through the virtual space.

### 3. VISUALIZATION

The system broadly follows the datapath shown in Figure 3.1. It begins with the user's thought of motion. An EEG machine then records the electrical signals emitted from the brain that results from their thoughts. The EEG recording is then sent into a signal-processing module that will preprocess the data. Following the signal processing module, the clean data goes into a machine learning algorithm to classify the user’s different motion-related thoughts. The virtual space is then updated based on the predictions the machine learning algorithm made.
Figure 3.1: Pictured above is a flow chart showing the flow of

data through the system, tracking the User’s thought to the virtual space.

### 3.1 EEG Recording

In order to extract the EEG from the brain we will need an apparatus that rests on the user’s head and records their brain's electrical activity. This apparatus would be optimally positioned to read the portions of the brain linked with pre-motion activity (electrical signals that precede actual bodily movements). A conceptual drawing of the apparatus can be found below in figure 3.2.

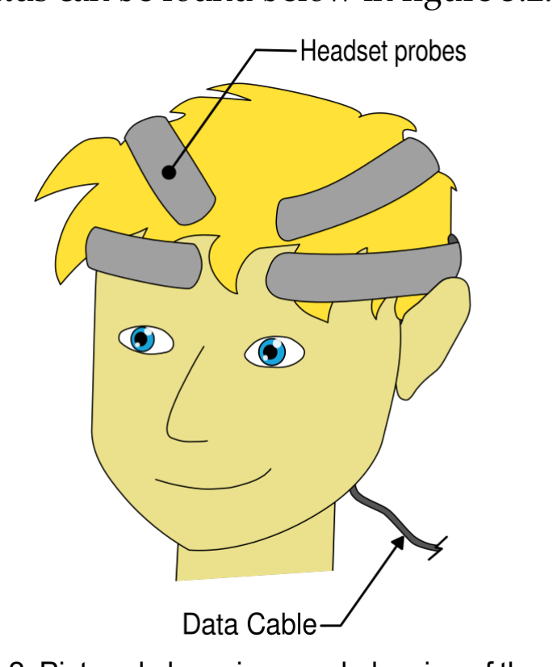
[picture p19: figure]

Figure 3.2: Pictured above is a mock drawing of the apparatus that would integrate the EEG reader into a wearable device.

### 3.2 Signal Processing

The raw EEG inherently has artifacts introduced from variations in the system and from the own user. For instance, EEGs vary in structure based on age and the presence of psychological conditions. They can also have artifacts from involuntary movements such as blinking. The literature points to advanced signal processing techniques as a viable and even suggested method of correcting the waveforms.

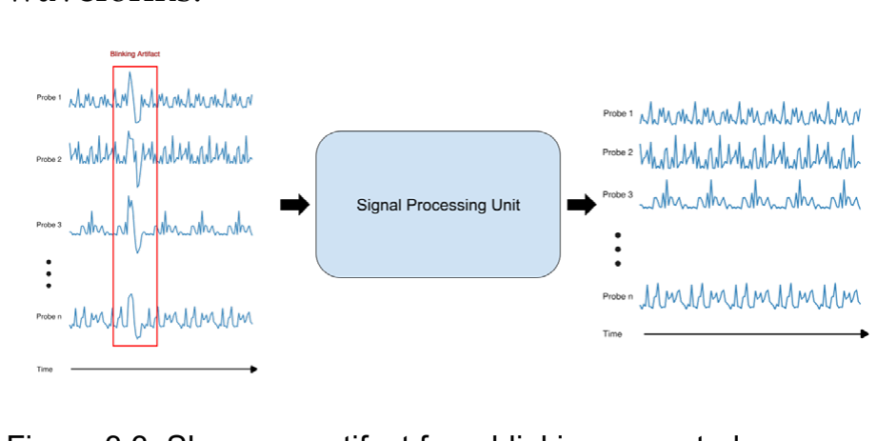
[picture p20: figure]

Figure 3.3: Shows an artifact from blinking corrected.

### 3.3 Machine Learning Inference

The processed EEG waveforms are dense in information, but there is no intuitive method of determining what in the waveform corresponds to the motions of interest. Therefore it makes sense to use a machine learning algorithm to find an optimal way of identifying the presence and type of motion in the EEG.

EC 463 – BOSTON UNIVERSITY ELECTRICAL & COMPUTER ENGINEERING CAPSTONE SENIOR DESIGN PROJECT | 4

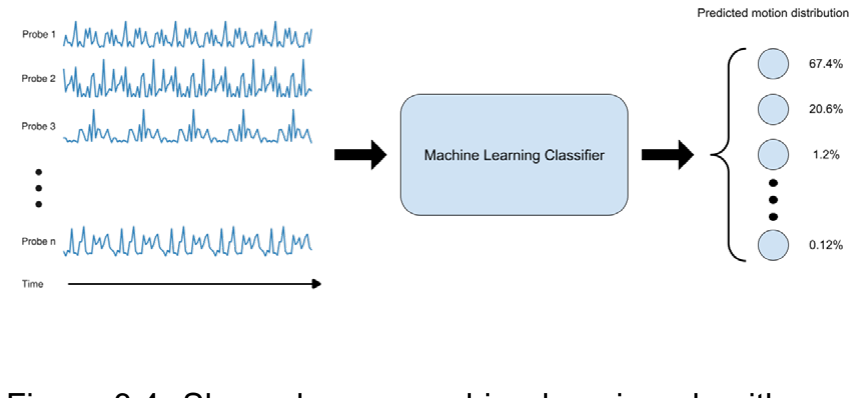
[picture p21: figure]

Figure 3.4: Shows how a machine learning algorithm maps time series information to a classification probability distribution.

### 4. COMPETING TECHNOLOGIES

The competing technologies in the brain-computer interface industry are described under three categories: EEG-based devices, invasive electrode
technology, | and | alternative | non-invasive
approaches. Since brain-computer interfacing is a new industry, much of the work has been completed for research purposes, and there is only a small subset of companies with products on the market. There are a vast number of US patents pertaining to wearable technology; however, machine learning algorithms are lawfully considered abstract ideas and are therefore ineligible for receiving patents in the United States [6].

### 4.1 Emotiv

The first category of competing technologies, EEG based devices, applies closest to this project. Typically constructed as a wearable device, EEG devices offer a low- risk, low- reward solution. Since the electrodes are placed atop the scalp, the signal to noise ratio is much lower when compared to invasive techniques.
Emotiv is the most established brain computer interface company in the industry. Founded in 2011, Emotiv offers non-invasive neuroheadsets and an accompanying software suite. They have four headsets on the market containing a range of two to thirty-two sensors on a single headset [7]. The Emotiv software can be trained to recognize a new command within twenty seconds and is capable of detecting six different emotions as well as twelve facial expressions. Similar to this project, the headsets contain a control unit that samples up to thirty-two channels with an applied bandpass filter. The data is wirelessly transmitted to the user’s computer containing an easy-to-use graphical interface for further processing. This project will incorporate only action commands, and will likely utilize fewer sensors. Though this project will contain only six designated actions, creating a flexible algorithm to account for new actions will be a stretch goal. Some of Emotiv’s headsets have adjustable sensor locations. This allows the user to read from different locations on the scalp for their intended purpose. This project will likely have a static placement of sensors; However, it may be beneficial to create the headset in this manner for experimental purposes.

### 4.2 Neuralink

The next category pertains to technologies that take an invasive approach to designing a brain computer interface. An invasive approach comes with significant complications that non-invasive approaches do not. For example, the device must be made of materials that can withstand the brain environment within the brain, and surgical methods of placing electrodes must be done as safely as possible.
Neuralink is the most popularized company in the brain-computer interface industry. Though Neuralink does not have any products in the market, it has made substantial steps in developing their invasive device. Neuralink is developing a robotic device that can accurately and quickly place electrode wires through a single twenty-five millimeter opening in the skull. Neuralink will use a chip containing one thousand electrode wires capable of wireless charging and complex signal processing. Since there is a large amount of data passing through this chip, the chip simplifies the raw electrical input into neural spikes to reduce power consumption [8]. This project does not need to deal with these complications in the same manner. However, electrode placement and signal processing are significant challenges that must be addressed. A unique implementation only achieved via invasive approaches is neural stimulation. By sending an electrical signal through the electrodes, action potentials in surrounding neurons can be induced. Neuralink hopes to use this process to create patterns of activity within the brain to elicit a desired sensation.

### 4.3 Kernel

The last category contains non-invasive techniques that do not utilize EEGs. The fundamental science behind this upcoming device is described as time-domain functional nearinfrared spectroscopy, or TD-fNIRS. This technique

EC 463 – BOSTON UNIVERSITY ELECTRICAL & COMPUTER ENGINEERING CAPSTONE SENIOR DESIGN PROJECT | 5

measures changes in hemoglobin levels within the
brain, | allowing | accurate, | high-resolution
observations of neural activity [9]. This method is
more complex and more expensive than EEGs. However, it is considered the gold standard of noninvasive optical imaging.
Kernel is the first company to create a wearable headset that utilizes TD-fNIRS for optical neural imaging. When designing their device, Kernel had to ensure full-head coverage, scalability, relatively-low cost, and freedom of user motion. Though the fundamental technology is different, these design constraints are universal. Similar to the Emotiv headset, this device has a signal-processing chip mounted to the headset. This allows for the user’s greater flexibility, but it does require the wireless transmission of data. Our design has a standalone unit to reduce the headset weight and limit the potential issues surrounding wireless transmission. However, in future iterations of our design, it may be beneficial to mount the signal processing chip onto the headset itself.

### 5. ENGINEERING REQUIREMENTS

The requirements for this surround modern issues with developments in hardware and software. For ease of use, transmissibility, and overall speed, these requirements will be essential for a safe and accurate deployment.

### 5.1 Hardware

1. The headset and connected cables must not weigh more than 1 kg.
2. The headset must fit a human head with a maximum circumference of 62 cm.
3. The headset must resist water and dust at a minimum IP54 equivalent level.
4. The total cost of the hardware must not exceed 250 USD.

### 5.2 Virtual Environment

1. The screen refresh rate must be at least 60
| Hz.
2. In response to a user’s choice of action, the on-screen delay must be less than 500 ms.
3. Using a desktop computer with at least 8 GB ram and an NVIDIA 1000 Series GPU (or equivalent), the virtual environment should run at minimum 60 fps.
4. Should not use more than 25% of the CPU’s
| memory.

### 5.3 Machine Learning Model

1. Be able to classify a user’s choice of action within 100 ms.
2. Algorithm must have a best-case efficiency of at least O(nlogn).
3. Achieve 75% accuracy when classifying a user’s input.

### 6. APPENDIX A REFERENCES

[1] S. Saha et al., “Progress in Brain Computer Interface: Challenges and Opportunities,” Frontiers in Systems
Neuroscience, | vol. | 15, | Feb. | 2021, | doi:
10.3389/fnsys.2021.578875.
[2] L. R. Hochberg, “Intracortical Brain-Computer Interfaces for the Restoration of Communication and Mobility,” Biophysical Journal, vol. 104, no. 2, p. 376a, Jan. 2013, doi: 10.1016/j.bpj.2012.11.2094.
[3] V. S. Polikov, P. A. Tresco, and W. M. Reichert, “Response of brain tissue to chronically implanted neural electrodes,” Journal of Neuroscience Methods, vol. 148, no. 1, pp. 1–18, Oct. 2005, doi: 10.1016/j.jneumeth.2005.08.015.
[4] “Brain Computer Interface Market Size | Industry Report,
2027,” | Available:www.grandviewresearch.com.
https://www.grandviewresearch.com/industry-analysis/brain-computer-interfaces-market
[5] J. Shih, D. J. Krusienski, and J. R. Wolpaw, “Brain-Computer Interfaces in Medicine,” Mayo Clinic Proceedings, vol. 87, no. 3, pp. 268–279, Mar. 2012, doi: 10.1016/j.mayocp.2011.12.008.
[6] A.Rapacke, “Are Machine Learning Algorithms Patentable?” The Rapacke Law Group, Mar. 15, 2021. Available:https://arapackelaw.com/patents/softwaremobileapps/are-machine-learning-algorithmspatentable/#:~:text=According%20to%20U.S.%20patent%20la w, (https://arapackelaw.com/patents/softwaremobile-apps/are-machine-learning-algorithms-patentable/)machine%20software%20and%20software%20patents (https://arapackelaw.com/patents/softwaremobile-apps/are-machine-learning-algorithms-patentable/)
[7] | Emotiv, | Company | Website. | Available:
https://www.emotiv.com/emotiv-launcher/#
[8] | Neuralink, | Company | Website. | Available:
https://neuralink.com/approach/
[9] SPIE, “Kernel flow: A wearable device for noninvasive
optical | brain | imaging” | Jan. | 18, | 2022.
Available:https://spie.org/news/kernel-flow-a-wearabledevice-for-noninvasive-optical-brain-imaging?SSO=1 (https://spie.org/news/kernel-flow-a-wearable-device-for-noninvasive-optical-brain-imaging?SSO=1)

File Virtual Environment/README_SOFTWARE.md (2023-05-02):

# Requirements
Make sure to install the required Python libraries. Running the command `pip install -r requirements.txt` will download each of the required libraries to successfully execute this project.

# Virtual Environment

<p align="center"> 
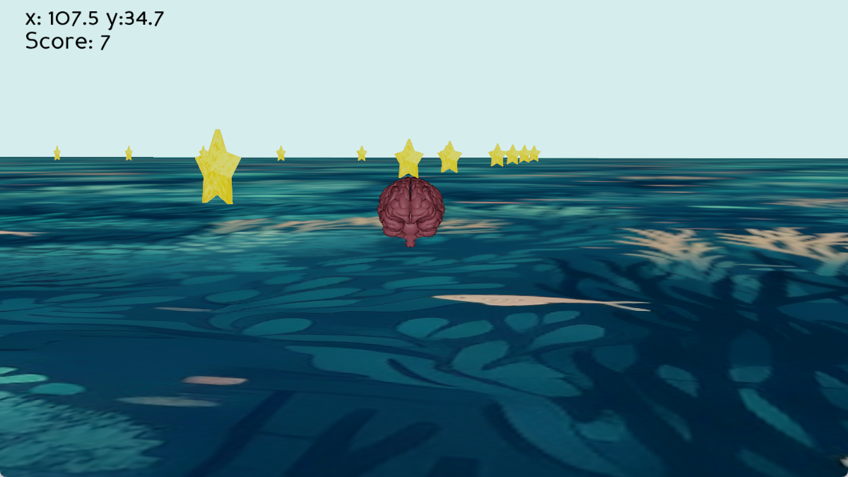
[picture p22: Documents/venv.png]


</p>

To run the virtual environment: Execute `python /Virtual Environment/main.py`

The main objective is to collect as many stars within a given timeframe.

A user may control the object using data received from the EEG, or can modify the functions to accept key inputs. See <a href="https://docs.panda3d.org/1.10/python/programming/index">Panda3D Documentation.</a >

# 2D Game

<p align="center">
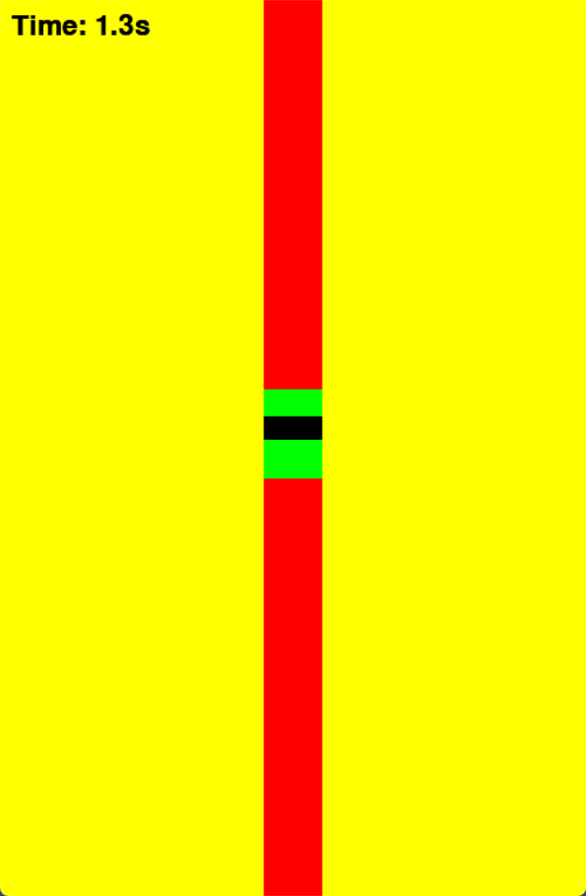
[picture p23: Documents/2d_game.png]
</div> </p>

The main objective of this game is to keep the black box within the green bar for as long as possible. The EEG will use power density concentration measurements to determine the adqueate  placement of the black box. The higher the concentration, the higher the box will go up the red bar.

# 30s Game

Almost identical to the 2D Game, except there is  a 30 second timer as well as random placement of the green box every 5 seconds.

# Data Collection GUI

To run GUI: Execute `python /Data\ Collection/main.py`

The GUI presents 2 options. Selecting "Imagery" will assume that the EEG will be classifiyng motor-imagery tasks. Selecting "Real" implies the actual movement of the instructed task.

# Useful Resources

* <a href='https://docs.panda3d.org/1.10/python/index'>Panda3D</a>
* <a href='https://www.pygame.org/docs/'>Pygame</a>
* <a href='https://docs.python.org/3/library/tkinter.html'>Tkinter</a>

For a more thorough view on software, including visual aid, you can access our <a href="https://github.com/BostonUniversitySeniorDesign/brain-4ce/blob/main/Documents/Team%204%20User's%20Manual.pdf">User's Manual.</a>

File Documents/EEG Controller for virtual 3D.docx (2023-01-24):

EEG-Based Controller for Navigating a Virtual 3D Space

Team Members: Brendan Shortall, Jonathan Mikalov, Mitchell Gilmore, TBD

The idea of controlling objects in a 3D space using nothing but the mind has been fantasized by science fiction for decades. In addition to the unlimited potential of electroencephalogram(EEG)-based controllers in the medical field, these devices could be utilized in almost every industry. Applications include but are not limited to, neural cognitive prosthetics, operating robotics, and virtual realities such as the Metaverse.

Invasive EEG devices have been used in the past to allow monkeys to navigate 3-dimensional spaces. However, an invasive EEG comes with significant risks. Infections, and other damage to the subject’s brain are major problems associated with an invasive EEG, as well as the cost and complexity of creating a device capable of withstanding the environment within the scalp. For these reasons, a non-invasive approach is most practical and has greater potential to reach those who cannot afford expensive surgeries.

In the past, teams have achieved 3-dimensional navigation using non-invasive EEGs both in a virtual world and in the physical world. In these cases however, the object at hand had a constant forward velocity. This allowed users to be able to pay more attention to the direction of the object rather than its entire motion. For this project, we will give the user full control of the object’s movement.

The device we will deliver will utilize methodologies from electrical, mechanical, hardware and software engineering. The physical device will be a headset that have EEGs placed in specific locations around the user’s head. The location of these EEGs will be determined by where we can achieve the strongest readings for the targeted brain functions. From there, the information read by the EEGs will be passed into a machine learning algorithm that will determine the desired course of action from the user. Artifacts are signals read by the EEG that are not generated by the brain such as the user blinking their eyes. Precautions in the code will attempt to account for these artifacts and will be designed to limit the interruptions caused by said artifacts. Once an action is determined by the machine learning algorithm above a certain threshold of certainty, the 3D object will then perform the action desired by the user. The user will be able to watch the object move in real time on a screen, allowing for adjustments to be made. It will be crucial for the object to move in a continuous manner, rather than discrete robotic-like movements. Designing our code to accommodate for this will be one of the many challenges we will face moving forward. Nonetheless, this project will yield a cost-effective, technically efficient device capable of bringing science fiction into reality.

Deliverables:

- A headset containing a series of non-invasive EEG sensors that will:
  - Read neural activity from specific regions of the brain
  - Output data to a predictive algorithm
- An algorithm that:
  - Utilizes machine learning techniques to predict the users desired course of action.
  - Actions will include rotate clockwise, rotate counterclockwise, move up, move down, move forward, move backwards.
  - Each action will be associated with the user thinking about moving certain body parts in certain manners.
- Software to utilize information from the previous algorithm to control an object in a virtual 3D space.
- A virtual 3D space as well as a task for the user to complete (i.e. move object through a ring).

Potential for improvement:

- Allow control over a virtual human character in 3D space, rather than an inanimate object.
- Add capability of completing more complex tasks (i.e. walking, jumping, picking up items, etc.)
- Controlling a physical device like a drone.
- A program to improve the efficiency of the training process necessary to operate the device.

Sources:

https://www.ncbi.nlm.nih.gov/pmc/articles/PMC3619112/#:~:text=Through%20EEG%20data%20acquisition%2C%20the,motor%20commands%20can%20be%20predicted.

https://www.ncbi.nlm.nih.gov/pmc/articles/PMC3037732/

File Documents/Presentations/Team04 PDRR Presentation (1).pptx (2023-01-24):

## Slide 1

Non-invasive EEG device for controlling an object in a virtual 3D environment
Team 4: Alex, Brendan, Dayanna, Jonathan, Mitchell

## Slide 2

Problem Statement
- How can we predict physical movement based on neural activity?
- Invasive (implanted) EEGs are becoming more popularized
- Risk of infections and severe brain damage
- More accurate

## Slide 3

Visualization

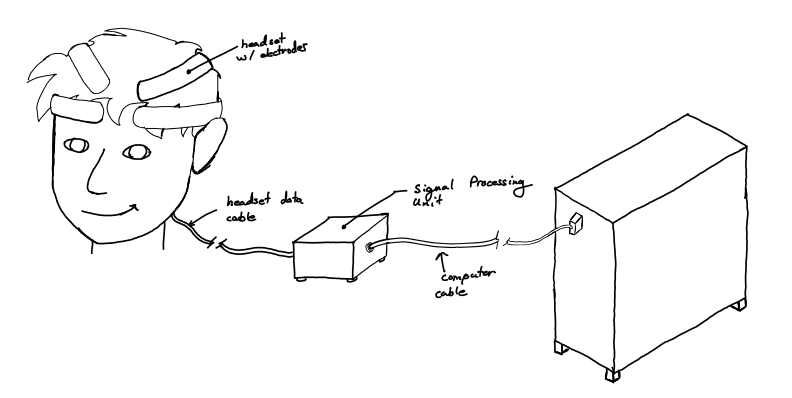
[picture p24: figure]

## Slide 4

Deliverables
- A headset
- Contains electrodes for specific parts of the brain to read signal activity
- Signal processing unit
- Machine learning algorithm
- Variation of Long Short-Term Memory (LSTM) algorithm
- Virtual 3D space: used to visualize predicted output from ML algorithm

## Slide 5

Requirements
- Lightweight, comfortable
- Compact
- Low latency
- Affordable, cost-effective

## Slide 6

Competing Technologies
- Neuralink (2016)
- Kernel (2016)
  - TD-Functional near-infrared spectroscopy
- EMOTIV (2011)
  - Patent US 10108264 B2 - Method for content personalization
  - Patent US 10028703 B2 - Wearable system for measuring biosignals
- U.S. Government patent 9050200 - BCI Neuroprosthetic
- University of Minnesota

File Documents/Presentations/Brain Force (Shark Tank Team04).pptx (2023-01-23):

## Brain Force

Where thoughts become motion.

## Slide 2

Our project, Brain Force, is an EEG-based brain computer interface that will be capable of recognizing an act based on thoughts of movements. To display its functionality, a user is presented with challenges in a virtual 3D environment that they must complete using their thoughts.

## Value Proposition

A. Many disabled individuals can not afford invasive brain-computer interface equipment.
B. Invasive technologies come with a wide array of risks and include frequent medical testing.
C. Disabled users may have difficulty operating a computer physically.
Brain Force will help a wide variety of disabled individuals navigate computer tasks, some of which are not supported by invasive technologies.

## BCI Illustration

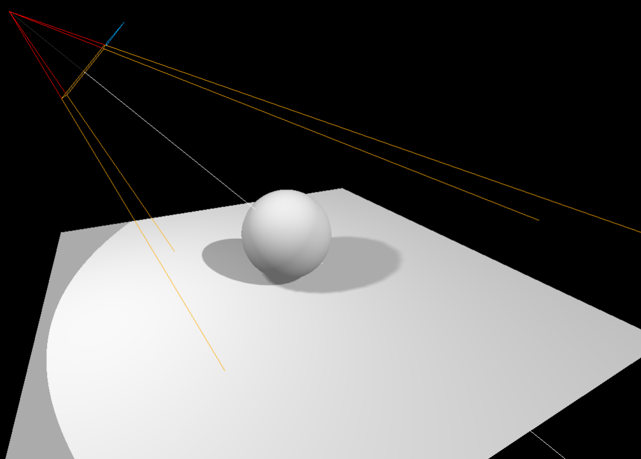
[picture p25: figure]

## MVP

ML Algorithm:
- Detects signals and classifies 4 commands (up, down, left, right) with 60% accuracy
- Control cursor with those commands
Headset:
- Adjustable and easily placed/removed
- Non-intrusive/comfortable

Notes: Minimum Viable Product

## System Overview Visualization:

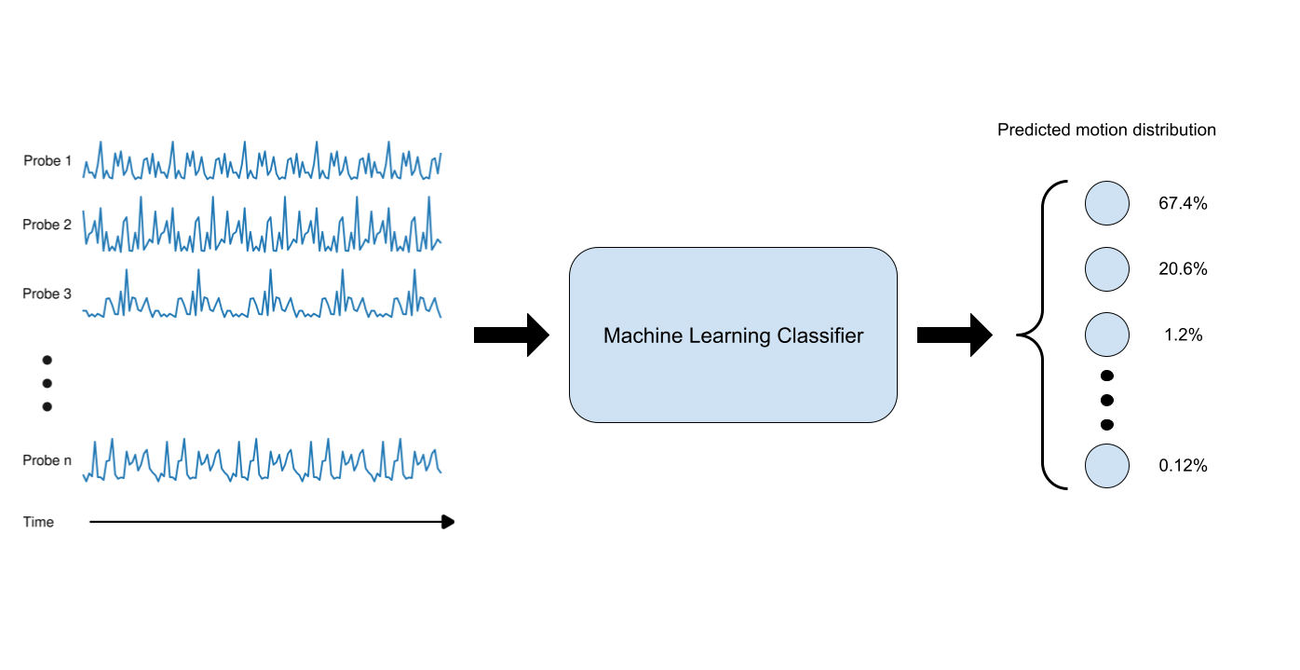
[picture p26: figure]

## System Overview:

- Wet or semi-dry EEG Sensors
- Chip capable of sampling, filtering, and amplification.
- Major signal processing will be computed on the computer’s GPU.
- BCI2000 software suite for analyzing data in real time
- The machine learning algorithm will utilize Python and accompanying libraries:
  - PYEEG - Feature extraction library for EEG data
  - PyTorch - Deep learning library
- 3D environment modeling using Panda 3D (Python library)

## User Stories

1. A paralyzed individual can use “Brain Force” technology to operate a computer cursor and perform operations
2. An immunocompromised individual who can not use invasive technologies can use this technology as a safer alternative

## Questions?

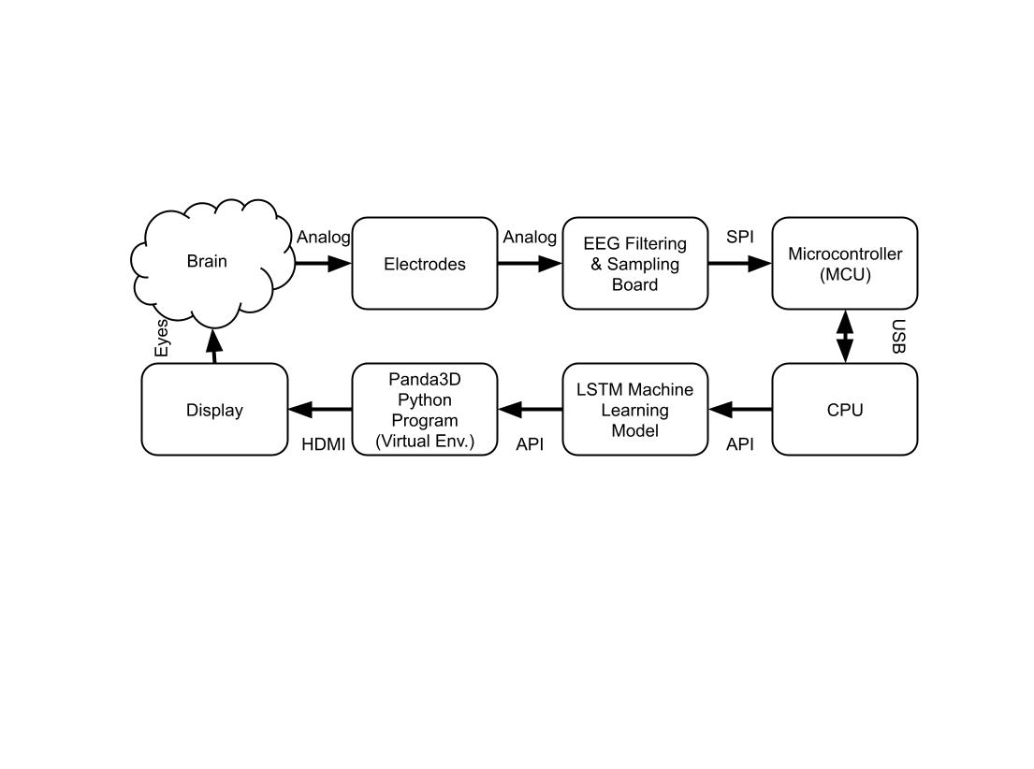
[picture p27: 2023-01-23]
Documents/First Semester Report 2022/System Block Diagram.jpg

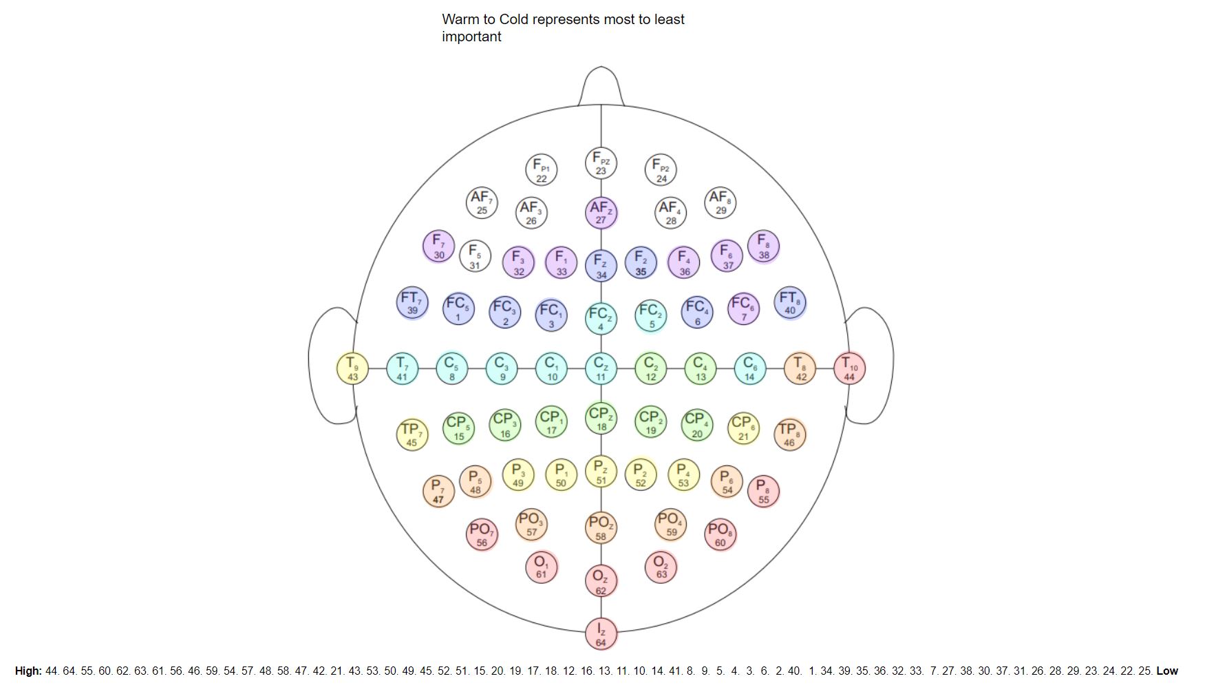
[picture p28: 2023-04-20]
Physionet Dataloader/Channel Placement.JPG

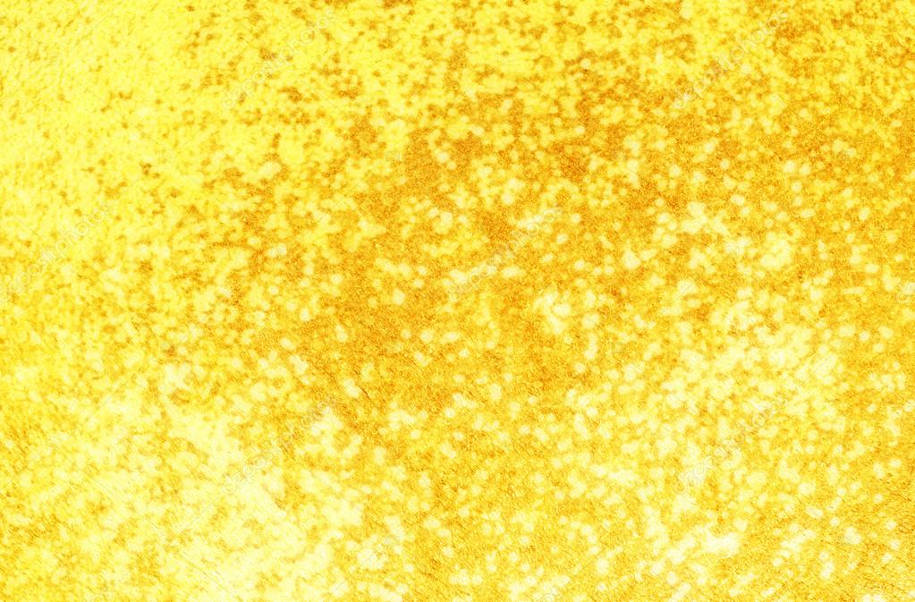
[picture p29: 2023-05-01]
Virtual Environment/models/star_texture.jpg

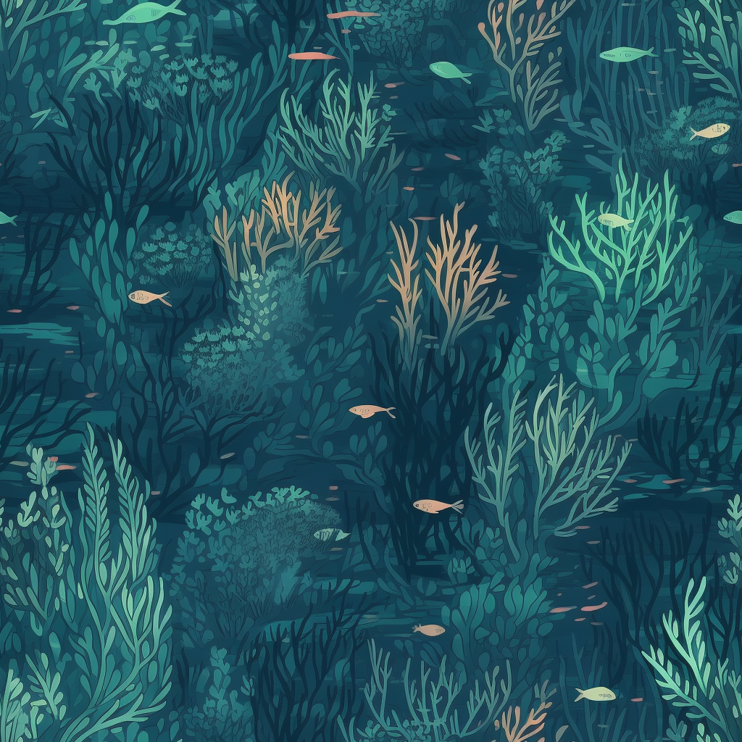
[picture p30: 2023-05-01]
Virtual Environment/models/water.png

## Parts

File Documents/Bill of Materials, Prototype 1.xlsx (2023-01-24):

 |  |  |  |  |  |  |  | For Record Keeping: |  |  | Receipt: | Who Ordered:
Part Description | Part Number | Quantity | Unit Cost | Tax/Shipping | Subtotal | Link | Alternate Part Link | In My Cart | Received | Notes
3/8" Medium Elastics | B08NCVLL2M | 1 pk (500pcs) | $8.99 | $0.00 | $8.99 | https://www.amazon.com/gp/product/B08NCVLL2M/ref=ppx_yo_dt_b_asin_title_o00_s00?ie=UTF8&psc=1 |  | Ordered | y | Will not count towards reimbursment |  | Brendan
1m Gold Cup Electrodes | 8544.42 | 1 (10 electrodes) | $29.75 | $12.91 | $42.66 | https://shop.openbci.com/products/openbci-gold-cup-electrodes?variant=37345591591070 |  | ordered | y |  |  | Brendan
Ten20 Conductive Paste | 3801.3 | 1 8oz Jar | $16.99 | $0.00 | $16.99 | https://shop.openbci.com/products/ten20-conductive-paste-8oz-jar?variant=37511929659550 |  | ordered | y |  |  | Brendan
18-8 Stainless Steel Pan Head Phillips Screw | 91772A084 | 1 (pack of 100) | $4.27 | $9.21 | $13.48 | https://www.mcmaster.com/91772A084/ |  | ordered |  |  |  | Jonathan
Disposable / Reusable Dry EEG Electrode |  | 1 (pack of 25) | $17.30 | $3.98 | $21.28 | https://fri-fl-shop.com/products/tde-200?variant=40151694540853 |  | ordered |  | Confirmation #PTUHW8DTN |  | Jonathan
18-8 Stainless Steel Hex Nut | 91841A003 | 1 (pack of 100) | $3.90 | $0.00 | $3.90 | https://www.mcmaster.com/91841A003/ |  | ordered |  |  |  | Jonathan
compression spring in 302/304 Stainless Steel |  | 17 | $2.44 | $10.14 | $51.62 | https://www.mwcomponents.com/shop/u-4cs |  | ordered |  | Order Id 2116882 |  | Jonathan
Slotted/Phillips Rounded Head Screws | 90077A106 | 1 (pack of 100) | $2.31 | $0.00 | $2.31 | https://www.mcmaster.com/90077A106/ |  | ordered |  |  |  | Jonathan
Printed Circuit Board |  | 1 (Order of 5) | $7.00 | $9.05 | $16.05 |  |  | ordered | y |  |  | Mitchell
ADS1296IPAG |  | 12 | $25.31 | $28.98 | $332.70 |  |  | ordered | y |  |  | Mitchell
Components (Various) |  |  | $155.44 | $24.10 | $179.54 |  |  | ordered | n |  |  | Mitchell
 |  | Total Spent: | $680.53
 |  | Remaing Budget: | $319.47

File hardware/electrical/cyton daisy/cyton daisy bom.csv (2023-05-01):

# | Reference | Qty | Value | Footprint | DNP
1 | C1, C2, C3, C4, C5 | 5 | CA0508KRX7R9BB102 | Capacitor Arrays:CAPCAXE50P210X130X94-8N
2 | C6, C7, C8, C9, C11, C19, C20, C23, C24 | 9 | 1uF | Capacitor_SMD:C_0402_1005Metric
3 | C10, C14, C21, C22, C25, C26 | 6 | 0.1uF | Capacitor_SMD:C_0402_1005Metric
4 | C12 | 1 | 100uF | Capacitor_SMD:C_1206_3216Metric
5 | C13 | 1 | 10uF | Capacitor_SMD:C_0603_1608Metric
6 | C15, C27 | 2 | 1nF | Capacitor_SMD:C_0402_1005Metric
7 | D1, D2, D3, D4, D5, D6 | 6 | TPD4E1B06DCKR | TSV - Diodes:TPD4E1B06DCKR
8 | J1 | 1 | Conn_02x13_Odd_Even | Connector_PinHeader_2.54mm:PinHeader_2x13_P2.54mm_Horizontal
9 | J2 | 1 | Conn_01x08 | Connector_PinSocket_2.54mm:PinSocket_1x08_P2.54mm_Vertical
10 | J4 | 1 | Conn_01x02 | Connector_PinSocket_2.54mm:PinSocket_1x02_P2.54mm_Vertical
11 | R1, R2, R3, R4, R5 | 5 | CAY16-222J4LF | Resistor Arrays:RESCAF80P320X160X60-8N
12 | R6 | 1 | 1M | Resistor_SMD:R_0402_1005Metric
13 | R13 | 1 | 0 | Resistor_SMD:R_0402_1005Metric
14 | U1 | 1 | ADS129x | Package_QFP:TQFP-64_10x10mm_P0.5mm

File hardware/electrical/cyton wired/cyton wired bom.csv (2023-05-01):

# | Reference | Qty | Value | Footprint | DNP
1 | C1, C2, C3, C4, C5 | 5 | CA0508KRX7R9BB102 | Capacitor Arrays:CAPCAXE50P210X130X94-8N
2 | C6, C7, C8, C9, C11, C19, C20, C23, C24 | 9 | 1uF | Capacitor_SMD:C_0402_1005Metric
3 | C10, C14, C21, C22, C25, C26 | 6 | 0.1uF | Capacitor_SMD:C_0402_1005Metric
4 | C12 | 1 | 100uF | Capacitor_SMD:C_1206_3216Metric
5 | C13, C29, C30, C36, C38, C41 | 6 | 10uF | Capacitor_SMD:C_0603_1608Metric
6 | C15, C27 | 2 | 1nF | Capacitor_SMD:C_0402_1005Metric
7 | C16, C34 | 2 | 0.01uF | Capacitor_SMD:C_0402_1005Metric
8 | C17, C18 | 2 | 47pF | Capacitor_SMD:C_0402_1005Metric
9 | C28, C31, C32, C33, C35, C37 | 6 | 2.2uF | Capacitor_SMD:C_0402_1005Metric
10 | C39, C40 | 2 | 18pF | Capacitor_SMD:C_0402_1005Metric
11 | CONN1 | 1 | USB_B_Micro | Connector_USB:USB_Micro-B_Molex-105017-0001
12 | D1, D2, D3, D4, D5, D6 | 6 | TPD4E1B06DCKR | TSV - Diodes:TPD4E1B06DCKR
13 | D7, D8 | 2 | ESD_VARISTOR | Diode_SMD:D_0402_1005Metric
14 | D9 | 1 | TVS_D | TSV - Diodes:ESDALC6V1-1M2
15 | D10 | 1 | LED_RED | LED_SMD:LED_0603_1608Metric
16 | D11 | 1 | LED_GREEN | LED_SMD:LED_0603_1608Metric
17 | D12 | 1 | D_Zener | Diode_SMD:D_SOD-323
18 | D13 | 1 | LED | LED_SMD:LED_0603_1608Metric
19 | F1 | 1 | SM_FUSE | Fuse:Fuse_1812_4532Metric
20 | J1 | 1 | Conn_02x13_Odd_Even | Connector_PinHeader_2.54mm:PinHeader_2x13_P2.54mm_Horizontal
21 | J2 | 1 | Conn_01x08 | Connector_PinSocket_2.54mm:PinSocket_1x08_P2.54mm_Vertical
22 | J3, J5 | 2 | Conn_01x04 | Connector_PinSocket_2.54mm:PinSocket_1x04_P2.54mm_Vertical
23 | J4 | 1 | Conn_01x02 | Connector_PinSocket_2.54mm:PinSocket_1x02_P2.54mm_Vertical
24 | L1, L2 | 2 | CHOKE | Inductor_SMD:L_0402_1005Metric
25 | R1, R2, R3, R4, R5 | 5 | CAY16-222J4LF | Resistor Arrays:RESCAF80P320X160X60-8N
26 | R6 | 1 | 1M | Resistor_SMD:R_0402_1005Metric
27 | R7, R8 | 2 | 22 ohm | Resistor_SMD:R_0402_1005Metric
28 | R9, R10 | 2 | 1k ohm | Resistor_SMD:R_0402_1005Metric
29 | R11, R12 | 2 | 330 ohm | Resistor_SMD:R_0402_1005Metric
30 | R13 | 1 | 0 | Resistor_SMD:R_0402_1005Metric
31 | R14 | 1 | 1k | Resistor_SMD:R_0402_1005Metric
32 | R15, R16 | 2 | 470k | Resistor_SMD:R_0402_1005Metric
33 | SW1, SW2 | 2 | SW_Push | Button_Switch_SMD:SW_SPST_PTS810
34 | U1 | 1 | ADS129x | Package_QFP:TQFP-64_10x10mm_P0.5mm
35 | U2 | 1 | CP2102N-Axx-xQFN24 | Package_DFN_QFN:QFN-24-1EP_4x4mm_P0.5mm_EP2.6x2.6mm
36 | U3 | 1 | MCP1754T-3302E/OT | Package_TO_SOT_SMD:SOT-23-5
37 | U4 | 1 | LM2664 | Package_TO_SOT_SMD:SOT-23-6
38 | U5 | 1 | TPS7A24 | Package_TO_SOT_SMD:SOT-23-5
39 | U6 | 1 | TPS723xx-Q1 | Package_TO_SOT_SMD:SOT-23-5
40 | U7 | 1 | PIC32MX250F128B-I/SS | Package_SO:SSOP-28_5.3x10.2mm_P0.65mm
41 | Y1 | 1 | ABMM2-8.000MHZ-E2-T | ABMM:XTAL_ABMM2-8.000MHZ-E2-T

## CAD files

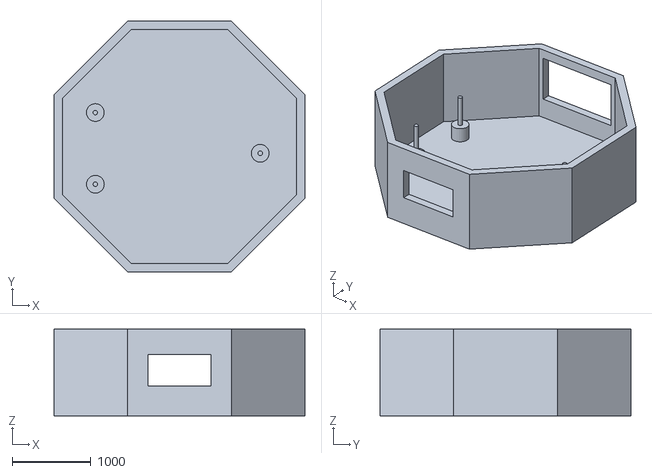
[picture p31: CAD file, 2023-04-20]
hardware/mechanical/CytonWired_CaseV1.stl
3186.8 x 3186.8 x 1100.0

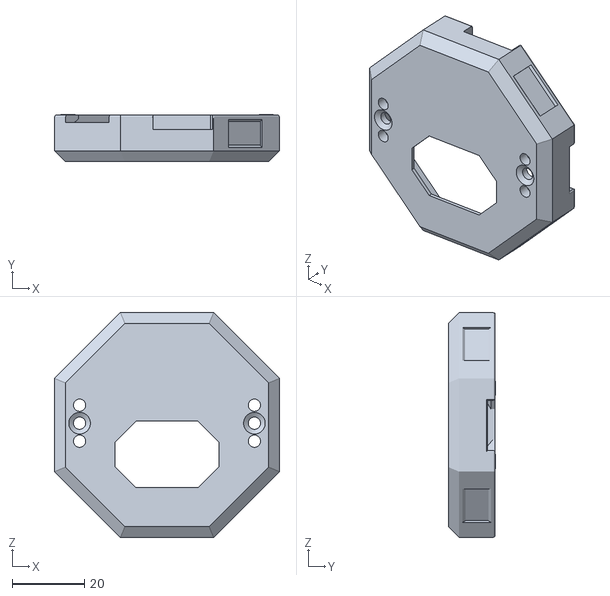
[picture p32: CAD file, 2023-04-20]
hardware/mechanical/Frame.stl
62.4 x 13.2 x 62.4

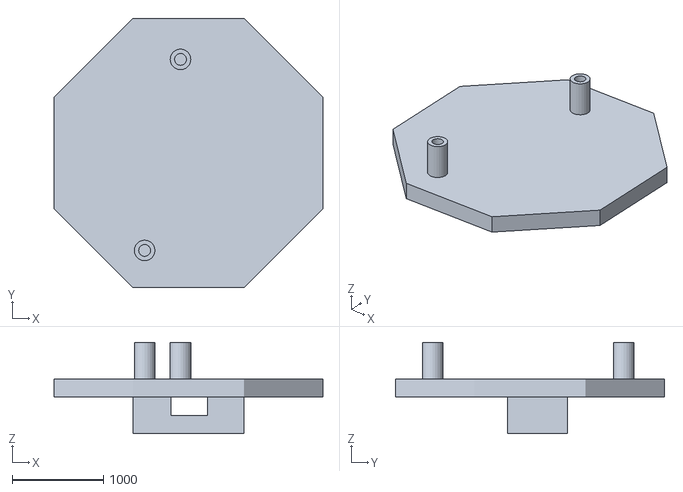
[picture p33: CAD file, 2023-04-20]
hardware/mechanical/CaseCover_V2.stl
2947.1 x 2947.1 x 1000.0

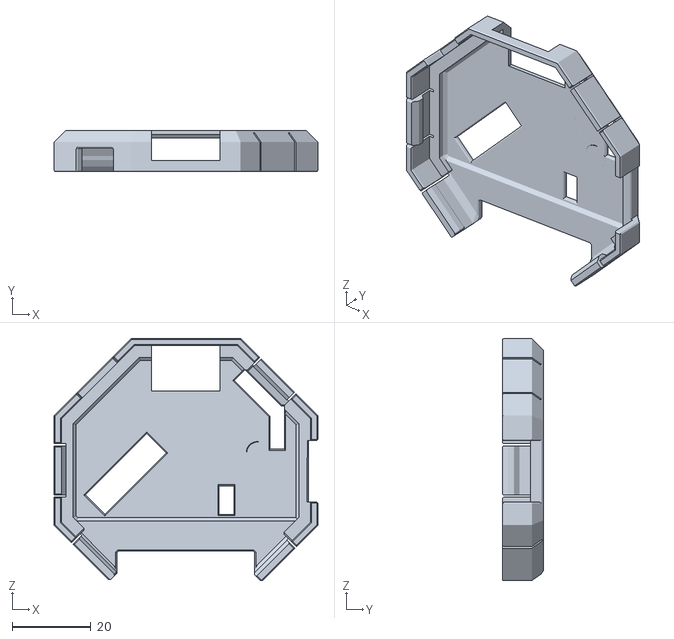
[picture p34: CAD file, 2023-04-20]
hardware/mechanical/Cover_V3.stl
67.1 x 10.5 x 61.5

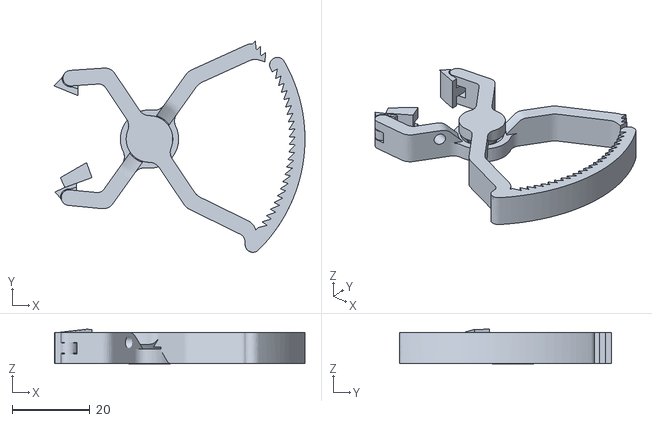
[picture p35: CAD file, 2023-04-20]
hardware/mechanical/Clip_wElectrode.stl
64.6 x 54.5 x 8.90

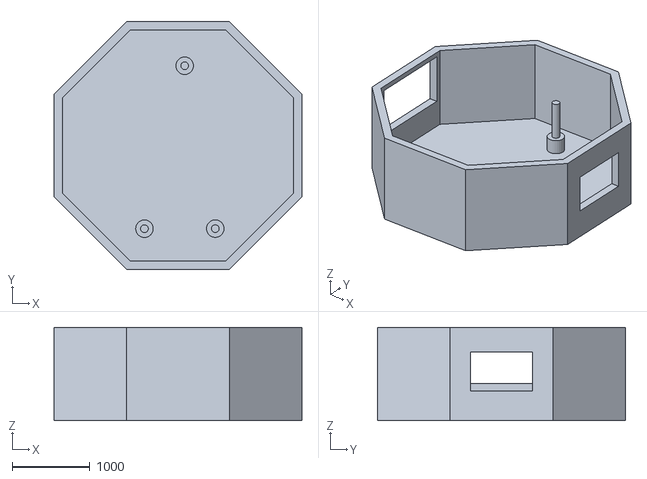
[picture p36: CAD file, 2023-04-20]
hardware/mechanical/CytonWired_CaseV2.stl
3186.8 x 3186.8 x 1200.0

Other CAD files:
hardware/mechanical/Case_Drawings.dwg
hardware/mechanical/Case_V3.stl

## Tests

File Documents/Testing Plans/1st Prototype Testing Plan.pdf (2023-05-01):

EC 463 – BOSTON UNIVERSITY ELECTRICAL & COMPUTER ENGINEERING CAPSTONE SENIOR DESIGN PROJECT | 1

## Boston University Electrical & Computer Engineering

EC463 Capstone Senior Design Project

## First Prototype Testing Plan

EEG-based Brain-Computer Interface

Submitted to:

Prof. Alan Pisano
apisano@bu.edu

by

Team 04
Brain Force

Team Members:

Alexander Johnson atjohnso@bu.edu Brendan Shortall shortall@bu.edu Dayanna De La Torres dayannat@bu.edu Jonathan Mikalov jmikalov@bu.edu Mitchell Gilmore mgilm0re@bu.edu

Submitted: 11/17/2022

EC 463 – BOSTON UNIVERSITY ELECTRICAL & COMPUTER ENGINEERING CAPSTONE SENIOR DESIGN PROJECT | 2

## Required Materials

Hardware:
- Handheld digital multimeter and test probes
- Oscilloscope
- Operational amplifiers
- Resistors / Capacitors
- Power supply
- Conductive paste
- Alligator clips

## Set Up

The goal of this testing is to ensure that the PCBs we have recently received have adequate connections and to measure an output of a single EEG sensor. In order to test the integrity of the PCB we will be using a handheld digital multimeter to conduct a series of continuity tests across vital components. To test the output of our EEG sensors we will build a simple amplifier circuit with a low pass filter to bring the raw voltage from tens of microvolts to a tens of millivolts range. We will connect the amplified output to an oscilloscope so we can view the sensor output in real time. We have not yet measured an output voltage from an EEG sensor, so any data we can receive will be considered a success. Multiple resistors may be on deck in case our gain is insufficient.

## Set Up Procedure

Testing the integrity of the PCB will take essentially zero setup. Just need a multimeter and a few wires to ensure it is working properly. We will also have a schematic of the PCB to ensure we are only testing the connections we are concerned with.
For the second part of our test, the EEG sensor, we will need to design a simple amplifier circuit using an OPAmp with a gain of around 1000x. A low pass filter will be applied using a series of capacitors. We will also need to hook up a power supply to the op amp and an oscilloscope to the voltage output. Before connecting the sensor, we can test the functionality of the circuit by using the power supply as an input and ensuring we get the expected output.

The schematic below shows the design of the PCB. We will be using this to decide where to test.

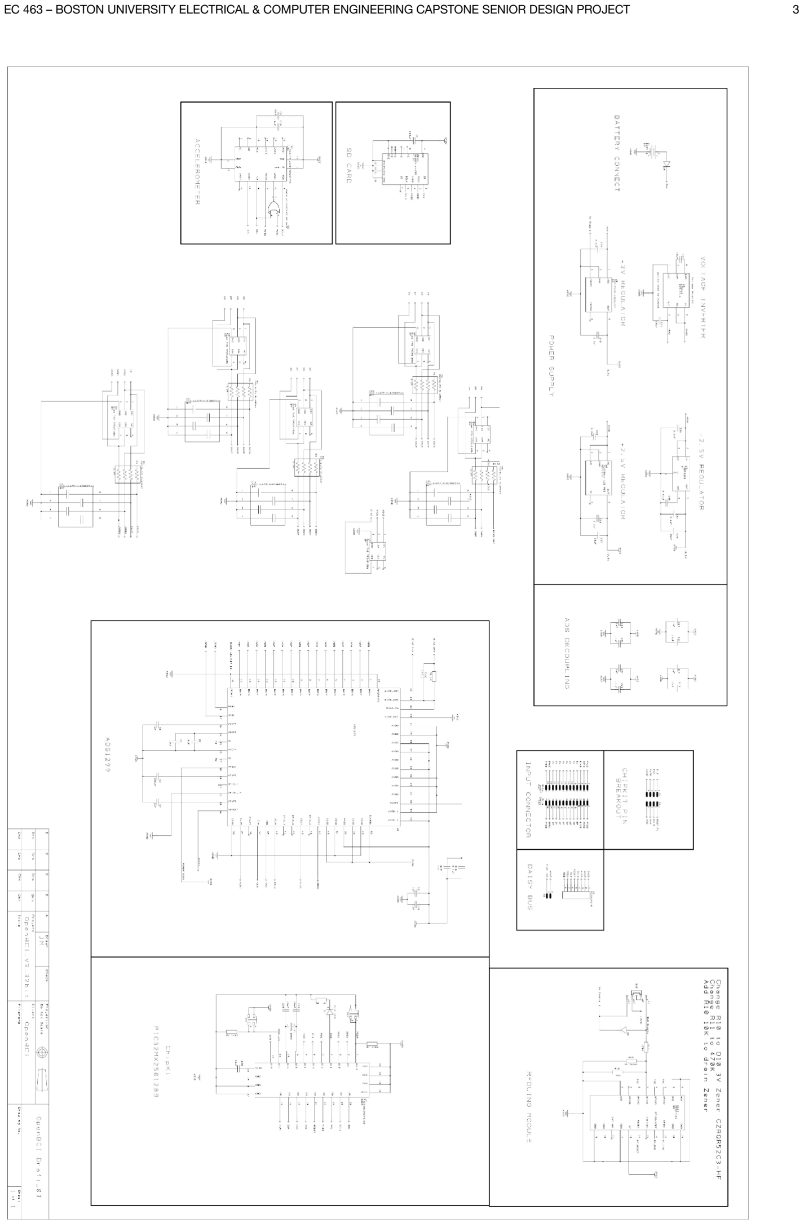
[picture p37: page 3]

EC 463 – BOSTON UNIVERSITY ELECTRICAL & COMPUTER ENGINEERING CAPSTONE SENIOR DESIGN PROJECT | 3

EC 463 – BOSTON UNIVERSITY ELECTRICAL & COMPUTER ENGINEERING CAPSTONE SENIOR DESIGN PROJECT | 4

## Testing Procedure

The testing procedure for the PCB includes:
1. Testing the multimeter on a single wire to ensure the continuity function works correctly.
2. Testing each component listed in the score sheet to ensure it is connected correctly. The result of each test will be recorded in the table below.
Testing the EEG Sensor will be done by:
1. Connect the power supply to the OpAmp, and hook up the oscilloscope to the correct location.
2. Use conductive paste to connect a single EEG sensor to a user’s scalp.
3. Connect the opposite end of the electrode wire to the OpAmp input.
4. See if we get an output on the oscilloscope.
5. If so, mark a few data points in an excel sheet and take a picture / video of the oscilloscope screen.
6. If we cannot get a reading, make sure all of the wires and connections are hooked up correctly.
7. If still no reading, try increasing the gain.

## Measurable Criteria

- Voltage output of OpAmp circuit
- Continuity of printed circuit board
- Number of working PCB components

## Score Sheet

Part Name: | Status (Y/N):

EC 463 – BOSTON UNIVERSITY ELECTRICAL & COMPUTER ENGINEERING CAPSTONE SENIOR DESIGN PROJECT | 5

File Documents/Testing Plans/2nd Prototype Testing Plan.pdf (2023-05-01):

EC 463 – BOSTON UNIVERSITY ELECTRICAL & COMPUTER ENGINEERING CAPSTONE SENIOR DESIGN PROJECT | 1

## Boston University Electrical & Computer Engineering

EC463 Capstone Senior Design Project

## Second Prototype Testing Plan

EEG-based Brain-Computer Interface

Submitted to:

Prof. Alan Pisano
apisano@bu.edu

by

Team 04
Brain Force

Team Members:

Alexander Johnson atjohnso@bu.edu Brendan Shortall shortall@bu.edu Dayanna De La Torres dayannat@bu.edu Jonathan Mikalov jmikalov@bu.edu Mitchell Gilmore mgilm0re@bu.edu

Submitted: 3/03/2023

EC 463 – BOSTON UNIVERSITY ELECTRICAL & COMPUTER ENGINEERING CAPSTONE SENIOR DESIGN PROJECT | 2

## Required Materials

Hardware:
- EEG Electrode Headset
- OpenBCI Cyton PCB
- USB-A to Micro-USB cable
- PIC32MX250F128B Microcontroller
- chipKIT UDB32-MX2-DIP bootloader
- ADS1296 Bio-sampling chip
- Multimeter + Probes

Software:
- OpenBCI GUI
- Arduino IDE
- OpenBCI Cyton Firmware Library
- Our Python code
- 3D Virtual environment:
- main.py: run simulation mechanics and control features
- generate.py: create 3D objects and lighting for the environment

## Set Up

The goal of this prototype testing is three-fold. The first and most important is to continue our active investigation into a bug in our system’s firmware. We have achieved two way communication between our computer and the on-board microcontroller. We will first ensure this communication channel is working properly. The main problem with the data communication channel is that we cannot receive input from the ADS1296 bio-sampling chip. We will first test the hardware connections in and out of this chip to ensure that the problem had not been overlooked in the PCB fabrication process. From there, we will look into our firmware and systematically debug in hopes of finding the cause of this issue.

The second goal of this prototype testing is to test our software that is responsible for receiving the data stream from the device. The goal of this software is to allow us to easily begin and end the data stream with the click of a button, and automatically store this data for later use. Once we have these two systems working independently, the output of this software will be fed into our neural network in real time.

This leads to the third and final goal of this prototype testing, the neural network and virtual environment. The network is currently in development and does not have many quantifiable

EC 463 – BOSTON UNIVERSITY ELECTRICAL & COMPUTER ENGINEERING CAPSTONE SENIOR DESIGN PROJECT | 3

parameters to test on, mainly due to the fact that we are not yet collecting our own data. Our virtual environment is also in development, but we are hoping to emulate a stream of actions that would come from the neural network in order to test the overall functionality of the virtual environment.

## Set Up Procedure

Set up for testing our hardware will begin by collecting all of the materials needed to test this system. These materials are listed above. We will then begin by compiling firmware and uploading to the microcontroller that tests if we have two-way communication between the chip and our computer. If this works, we will then include firmware that retrieves data from the sampling chip. We will compile and upload this new firmware to the board, and connect to the OpenBCI GUI. If the output is as expected, we will plug into the headset and perform further tests. If not, we will debug the system to find the reason why.

Testing the software is fairly straightforward. There will be three command line functions to test, start_stream(), end_stream() and stream(n) where n is the number of seconds to stream for. For each of these functions we will make sure that data is output to the proper place, and that the data is formatted correctly.

Testing our virtual environment will need a series of test cases that emulate output from the neural network. This will likely be a command labeled 0-3 (inclusive) input into the datastream every second or so. Multiple command sequences will be tested in order to ensure that there are no bugs within the system.

## Testing Procedure

The testing procedure for the PCB includes:
1. Begin by ensuring that power is being sent to the board
2. Reupload firmware
3. Test if we can create a data stream between microcontroller and computer
4. If success, try to get data from sampling chip
5. If successful, plug into the headset and test the quality of signals.
6. If successful, plug into the software script and stream data on command.
7. Else debug and repeat
The testing procedure for the software includes:
1. Loading up the python script

EC 463 – BOSTON UNIVERSITY ELECTRICAL & COMPUTER ENGINEERING CAPSTONE SENIOR DESIGN PROJECT | 4
2. Ensure that it compiles properly and that all dependencies are installed
3. Execute the start function
4. Execute the stop function
5. Check data output
6. Execute the start(n) function
7. Check data output
8. Test on our board if possible
The testing procedure for the virtual environment includes:
1. Load virtual environment script
2. Ensure test cases fully test the script
3. Run environment with keyboard commands
4. Run a test case and make sure the environment updates properly
5. Evaluate and repeat

## Measurable Criteria

- Hardware
- Continuity between necessary pins
- Data stream between computer and microcontroller
- Firmware compiles?
- Can we get data onto the computer?
- Functionality of software functions
- Start
- Stop
- start(n)
- Functionality of virtual environment
- Test cases
- Inputs 0-3 correlating to model output

## Score Sheet

Hardware:

Function: | Works?

Power?

Continuity?

Communication w/ Microcontroller?

EC 463 – BOSTON UNIVERSITY ELECTRICAL & COMPUTER ENGINEERING CAPSTONE SENIOR DESIGN PROJECT | 5

Communication w/ sampling chip?

Works w/ Sensors?

Works w/ scripts?

Software:
Function: | Works? (Y/N)

begin_stream()

end_stream()

stream(n)

Virtual Environment:
Test Case: | Valid output? (Y/N)

Test 1

Test 2

Test 3

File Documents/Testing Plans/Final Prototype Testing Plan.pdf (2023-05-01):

EC 464 – BOSTON UNIVERSITY ELECTRICAL & COMPUTER ENGINEERING CAPSTONE SENIOR DESIGN PROJECT | 1

## Boston University Electrical & Computer Engineering

EC464 Capstone Senior Design Project

## Final Prototype Testing Plan

EEG-based Brain-Computer Interface

Submitted to:

Prof. Alan Pisano
apisano@bu.edu

by

Team 04
Brain Force

Team Members:

Alexander Johnson atjohnso@bu.edu Brendan Shortall shortall@bu.edu Dayanna De La Torres dayannat@bu.edu Jonathan Mikalov jmikalov@bu.edu Mitchell Gilmore mgilm0re@bu.edu

Submitted: 4/06/2023

EC 464 – BOSTON UNIVERSITY ELECTRICAL & COMPUTER ENGINEERING CAPSTONE SENIOR DESIGN PROJECT | 2

## Required Materials

Hardware:
- EEG Electrode Headset
- 12 electrode probes with housing
- Cyton board case and cover
- Cyton PCB
- USB-A to Micro-USB cable
- PIC32MX250F128B Microcontroller
- ADS1299 Bio-sampling chip Software:
- OpenBCI GUI
- 3D Virtual environment:
- main.py: run simulation mechanics and control features
- BrainFlow Streaming script
- ML test model
- Socket programs
- Data transfer between BrainFlow streaming scripts into ML model
- Data transfer between ML model and virtual environment

## Set Up

There are two main goals to this prototype testing. The first goal is to prove the functionality of the hardware. This will be composed of simultaneously testing the hardware and software that is responsible for receiving the data stream from the device. The goal of this software is to allow us to easily begin and end the data stream with the click of a button, and automatically store this data for later use. We will also be able to view, in real time, brain waves from our 8-channels on a monitor. The main difference between this test and our previous is that we hope to get output data that has distinguishable features rather than strictly noise.

The second goal is to successfully have socket connectivity between the different aspects of the project (the headset, neural network, and virtual environment). While the neural network is not completed, it has been simulated through a faux classification script. The goal of these socket programs will be to prove we can catch data from the headset in real time and that we can transfer data from the “neural network” to the virtual environment to emulate a stream of actions.

EC 464 – BOSTON UNIVERSITY ELECTRICAL & COMPUTER ENGINEERING CAPSTONE SENIOR DESIGN PROJECT | 3

## Set Up Procedure

Set up for testing our hardware will begin by connecting the Cyton board to the OpenBCI GUI to ensure that the hardware and firmware are working properly. We will also be testing the efficiency of the headset-board system by placing the headset on someone’s head and viewing the FFT plot of the channels. We hope to get values in the microvolt range that have some discrete artifacts.

Once we ensure the board is working properly, we will then connect it to our BrainFlow code. This code should allow the board to be plug and play, automatically detecting the board and COM port it is connected to. Once a connection has been established, we will then test the functionality of the BrainFlow code by starting a data stream.

We then want to test the entire system. This will consist of plugging in the headset, streaming data into the ML model, and sending the ML model output into the virtual environment. We should be able to see that in real time, the virtual environment will update based on the classification of the ML model.

## Testing Procedure

STAGE 1: The testing procedure for the PCB includes:
1. Begin by ensuring that power is being sent to the board indicated by the blue LED
2. Open the OpenBCI GUI and connect the board
3. Observe the FFT plot before the headset is connected
4. Connect the headset, and observe the FFT plot once more.
5. Compare differences, look for artifacts.
STAGE 2: Once we verify that this system is working correctly.
1. Disconnect the Cyton, Close the OpenBCI GUI
2. Open our streaming software, connect the device.
3. Ensure that the automatic board detection system works properly
4. Begin a data stream
5. Wait some time and end the stream
6. Check that the output data is as expected
STAGE 3: Now we begin to test the entire system
1. Boot up the socket code, the ML model, and the virtual environment
2. Plug in the headset and begin a stream
3. View each stage to ensure that the data is coming in/out as expected
4. View the virtual environment to see if it updates as expected

EC 464 – BOSTON UNIVERSITY ELECTRICAL & COMPUTER ENGINEERING CAPSTONE SENIOR DESIGN PROJECT | 4

## Measurable Criteria

Stage 1:
- Does the board receive power?
- Do we connect to the OpenBCI GUI?
- Can we view the FFT plot in real time, as well as the individual channels?
- What is the peak to peak magnitude of the signals?
- Once the headset is connected, can we notice a difference between the two? Stage 2:
- Does the script automatically detect the board is connected?
- Does it detect the correct COM port? (Try multiple ports)
- Does the stream begin when instructed?
- Does it end when instructed?
- Is the data received reasonable?
Stage 3:
- Does the BrainFlow code communicate with the ML model?
- Does the ML model communicate with the virtual environment?
- Can we see movement in the virtual environment?

## Score Sheet

Stage 1:

Test: | Results: | Comments:
Power received? | (Y/N)
Connected to GUI? | (Y/N)

Peak-to-Peak magnitude (Disconnected from headset)

Peak-to-Peak magnitude (Connected to headset)

Notice artifacts? | (Y/N)

EC 464 – BOSTON UNIVERSITY ELECTRICAL & COMPUTER ENGINEERING CAPSTONE SENIOR DESIGN PROJECT | 5

Stage 2:

Test: | Results: | Comments:

Automatic board detection

Test every COM port

Begin stream

End stream

Data reasonable?

Stage 3:

Test: | Results: | Comments:

BrainFlow to Model

Model to V.E.

V.E. updates?

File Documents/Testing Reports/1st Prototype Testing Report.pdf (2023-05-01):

EC 463 – BOSTON UNIVERSITY ELECTRICAL & COMPUTER ENGINEERING CAPSTONE SENIOR DESIGN PROJECT | 1

## Boston University Electrical & Computer Engineering

EC463 Capstone Senior Design Project

## First Prototype Testing Report

EEG-based Brain-Computer Interface

Submitted to:

Prof. Alan Pisano
apisano@bu.edu

by

Team 04
Brain Force

Team Members:

Alexander Johnson atjohnso@bu.edu Brendan Shortall shortall@bu.edu Dayanna De La Torres dayannat@bu.edu Jonathan Mikalov jmikalov@bu.edu Mitchell Gilmore mgilm0re@bu.edu

Submitted: 11/20/2022

EC 463 – BOSTON UNIVERSITY ELECTRICAL & COMPUTER ENGINEERING CAPSTONE SENIOR DESIGN PROJECT | 2

## Equipment & Setup Summary

For the actual setup of this procedure, we utilized all required materials needed for testing the experiment. In order to obtain proper readings of the EEG electrodes, we had to amplify our voltage output by 900x. To amplify the voltage output, we created a differential amplifier circuit using a set of resistors, a 5V power supply, and an MCP6002 operational amplifier. As an additional setup, electrode wires were connected to the voltage output of the circuit in order to obtain a potential physiological response from a test subject.

## Experimentation Procedure

In order to test the performance of the EEG electrodes, we attached them to the test subject’s arm using conductive paste. For a second trial, we detached them from the arm and placed them directly on the forehead to examine a potential change in results. As an additional test, we also used conductive paste for testing the EEG electrodes onto another subject’s forehead.
For all the trials, we made sure to abide by all safety requirements as per lab guidelines and made sure to operate within reasonable voltage (5V).

## Results

Ultimately, we were unable to obtain readings from the EEG electrodes. The oscilloscope displayed a constant zero voltage regardless of the electrode placement on our test subject. We noticed a change in the output voltage when moving the electrodes with the input voltage turned off. These readings, however, were on the scale of microvolts, a negligible difference from the base zero voltage. We were also unable to test the PCB due to these limitations.

## Analysis

The small readings we were able to obtain on the oscilloscope were likely due to interference from the internal electronics of the oscilloscope, waveform generator, or power supply. Regarding the constant zero voltage readings, we anticipate inaccurate wiring, saturation of one or more components, or improper gain tuning to be the cause. We attempted to correct for the saturation and gain issues by changing the values of the resistors used in our differential amplifier. To ensure that we were not using a malfunctioning MCP6002 operational amplifier, we had also replaced it with another MCP6002. Unfortunately despite numerous circuit debugging attempts, we were not successful in witnessing accurate voltage reading measurements from the EEG electrodes. It is hoped that using our PCB design as well as more advanced circuit schematics from OpenBCI that we will obtain far more accurate and efficient patterns.

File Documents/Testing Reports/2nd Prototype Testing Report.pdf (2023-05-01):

EC 463 – BOSTON UNIVERSITY ELECTRICAL & COMPUTER ENGINEERING CAPSTONE SENIOR DESIGN PROJECT | 1

## Boston University Electrical & Computer Engineering

EC464 Capstone Senior Design Project

## Second Prototype Test Report

EEG-based Brain-Computer Interface

Submitted to:

Prof. Alan Pisano
apisano@bu.edu

by

Team 04
Brain Force

Team Members:

Alexander Johnson atjohnso@bu.edu Brendan Shortall shortall@bu.edu Dayanna De La Torres dayannat@bu.edu Jonathan Mikalov jmikalov@bu.edu Mitchell Gilmore mgilm0re@bu.edu

Submitted: 3/17/2023

EC 463 – BOSTON UNIVERSITY ELECTRICAL & COMPUTER ENGINEERING CAPSTONE SENIOR DESIGN PROJECT | 2

For the prototype test, our equipment was
composed of an EEG electrode headset, a
PIC32 microcontroller and bootloader, a bio-sampling chip, as well as a multimeter with probes. The software required for testing included the OpenBCI GUI, Arduino IDE, and Python code for the 3D virtual environment and machine learning library.

During the testing, our team had three goals. The first was to display a set of current challenges faced with the development of our project. For example, the firmware communication channel did not accurately interface between the computer and the microcontroller, since input from the bio-sampling chip was not being received. We displayed the hardware connections in and out of the chip and debugged the firmware to explore potential root causes of the issue.

The second goal was to demonstrate the software responsible for receiving data streams for the printed circuit board. The software needed to allow an easy start and stop of data streams as well as readability for debugging purposes. We demonstrated the software during prototype testing and displayed its core functionalities.

Lastly, we demonstrated a sample (tentative) LSTM-based neural network that will be used to classify our EEG brainwaves into predefined motor imagery tasks. We also displayed a virtual environment simulation that the user will eventually be able control using their mind. This simulation involved a sphere that could be moved in any direction.

We were able to measure the hardware through a variety of circuit-based characteristics. To ensure continuity between the necessary pins, voltage power was measured. Furthermore, communication between the sampling chip and microcontroller was evaluated to determine its functionality. Data streams in the software were also measured with Python functions, those being start_stream( ) and end_stream() to demonstrate the speed at which Python can process a set amount of example data. For the virtual environment, virtual coordinates were displayed in the simulation to display to the user how far they have moved across the screen compared to the origin (which is 0,0).

Conclusively, our 2nd semester prototype test displayed a variety of operations that can be performed by the hardware and software that we developed. Being able to showcase our methodology behind investigating root causes for hardware and software issues will be integral for the success of the project. Furthermore, our demonstration of the sample neural network and Python environment simulation showed the importance of the EEG electrode headset to the end-user. The ability to control a virtual system using predefined motor imagery tasks will prove to be a significant feat for a senior design project.

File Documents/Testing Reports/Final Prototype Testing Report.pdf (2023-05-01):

EC 464 – BOSTON UNIVERSITY ELECTRICAL & COMPUTER ENGINEERING CAPSTONE SENIOR DESIGN PROJECT | 1

## Boston University Electrical & Computer Engineering

EC464 Capstone Senior Design Project

## Final Prototype Test Report

EEG-based Brain-Computer Interface

Submitted to:

Prof. Alan Pisano
apisano@bu.edu

by

Team 04
Brain Force

Team Members:

Alexander Johnson atjohnso@bu.edu Brendan Shortall shortall@bu.edu Dayanna De La Torres dayannat@bu.edu Jonathan Mikalov jmikalov@bu.edu Mitchell Gilmore mgilm0re@bu.edu

Submitted: 4/13/2023

EC 464 – BOSTON UNIVERSITY ELECTRICAL & COMPUTER ENGINEERING CAPSTONE SENIOR DESIGN PROJECT | 2

Introduction:
This report outlines the results of the
prototype testing performed on our hardware and software designed for our senior design project. Our team aimed to achieve two primary goals during the testing: first, to verify the functionality of our hardware and software in receiving data streams from the EEG electrode headset and second, to establish socket connectivity between the different aspects of our project - the headset, neural network, and virtual environment.

Equipment:
The testing equipment consisted of an EEG electrode headset, 12 electrode probes with housing, a Cyton board case and cover, a Cyton PCB, a USB-A to Micro-USB cable, a PIC32MX250F128B Microcontroller, an ADS1299 Bio-sampling chip, the OpenBCI GUI, the main.py script for 3D virtual environment, the BrainFlow Streaming script, an ML test model, and socket programs for data transfer.

Setup:
The first goal of the testing was to ensure the functionality of the hardware and software designed for receiving data streams from the device. The setup procedure involved connecting the Cyton board to the OpenBCI GUI to verify the hardware and firmware's proper functioning. After this, we tested the efficiency of the headset-board system by placing the headset on someone's head and viewing the FFT plot of the channels. The aim was to observe distinguishable values in the microvolt range with discrete artifacts.

After the hardware verification, we connected the board to our BrainFlow code, which would detect the board automatically and establish a connection. We then tested the BrainFlow code's functionality by initiating a data stream. The next step was to test the entire system by plugging in the headset, streaming data into the ML model, and sending the ML model output to the virtual environment. In this stage, we aimed to observe the real-time virtual environment updates based on the classification of the ML model.

Testing Procedure:
Stage 1: We first ensured that the power was being sent to the board, indicated by the blue LED. After connecting the board to the OpenBCI GUI, we observed the FFT plot before and after connecting the headset. We compared the differences and looked for artifacts to ensure proper functioning.

Stage 2: After verifying the system's proper functioning, we disconnected the Cyton, closed the OpenBCI GUI, and opened our streaming software to connect the device. We tested the automatic board detection system and initiated a data stream to ensure proper functioning. Next, we established socket connectivity between the headset, neural network, and virtual environment. This involved testing data transfer from the headset to the neural network and then from the neural network to the virtual environment. We verified that the virtual environment updated in real-time based on the ML model classification.

EC 464 – BOSTON UNIVERSITY ELECTRICAL & COMPUTER ENGINEERING CAPSTONE SENIOR DESIGN PROJECT | 3

Conclusion:
The prototype testing of our hardware and
software designed for receiving data streams from the EEG electrode headset and establishing socket connectivity was successful. Our testing procedure verified the proper functioning of the hardware and software, and we were able to transfer data in real-time between the different aspects of the project. Overall, the prototype testing results were positive, and we are confident in the success of our senior design project.

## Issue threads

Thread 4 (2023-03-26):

### ISSUE TITLE
Debug LEDs for the RX and TX UART controller

### ISSUE THREAD

**Issue by mitch-gilmore** [BostonUniversitySeniorDesign/brain-4ce#4]
Currently the LEDs never turn on when sending serial information to and from the MCU. I suspect this is because insufficient current is passing through the device. In order to debug I purpose to first connect jumpers to the pull down resistors in order to view that the UART controller is falling low periodically when sending '?' over serial which requests all the registers in the ADC to be read out. If the probes are placed at the nodes between the resistors and the LED it should also allow for the current though the LED to determined.
![image](https://user-images.githubusercontent.com/102109623/227747535-ea32c876-02e6-4e13-a31d-982112ae85f5.png)

**Comment by atjohnson** [comment]
Hey @mgilmore42,

I measured the voltage at both nodes circled in the picture relative to ground and found them to be high at all times no matter what command is sent to the board. I'm getting roughly 3.191V at the VDD node and 3.165V at the D10 and D11 nodes.

**Comment by mitch-gilmore** [comment]
@atjohnson Did you use an oscilloscope or the DMM?

**Comment by atjohnson** [comment]
@mgilmore42 DMM. Should I try the oscilloscope too?

**Comment by mitch-gilmore** [comment]
@atjohnson generally speaking the DMM is ill suited for looking at transient signals. You should look at it with an oscilloscope.

**Comment by mitch-gilmore** [comment]
For traceability the problem was solved by editing the firmware of the UART controller. By default the GPIO pins default to inputs and do not flash the LEDs (see [datasheet here](https://www.silabs.com/documents/public/data-sheets/cp2102n-datasheet.pdf#unique_28)). This needed to be enabled in the controller firmware. This was accomplished by using [Simplicity Studio](https://www.silabs.com/developers/simplicity-studio) and in the _Xpress Configurator_ setting the GPIO pins 1 and 2 to their alternate functionality. @atjohnson can you provide a screenshot to aid others if they use our work later on?

**Comment by atjohnson** [comment]
The GPIO0 and GPIO1 signals were changed from an Alternate Function of "GPIO" to "TX Toggle" and "RX Toggle" respectively:
![GPIO Config](https://user-images.githubusercontent.com/75290142/227805672-a9a2dcd0-7f6f-4326-af84-172bca6844b4.jpg)

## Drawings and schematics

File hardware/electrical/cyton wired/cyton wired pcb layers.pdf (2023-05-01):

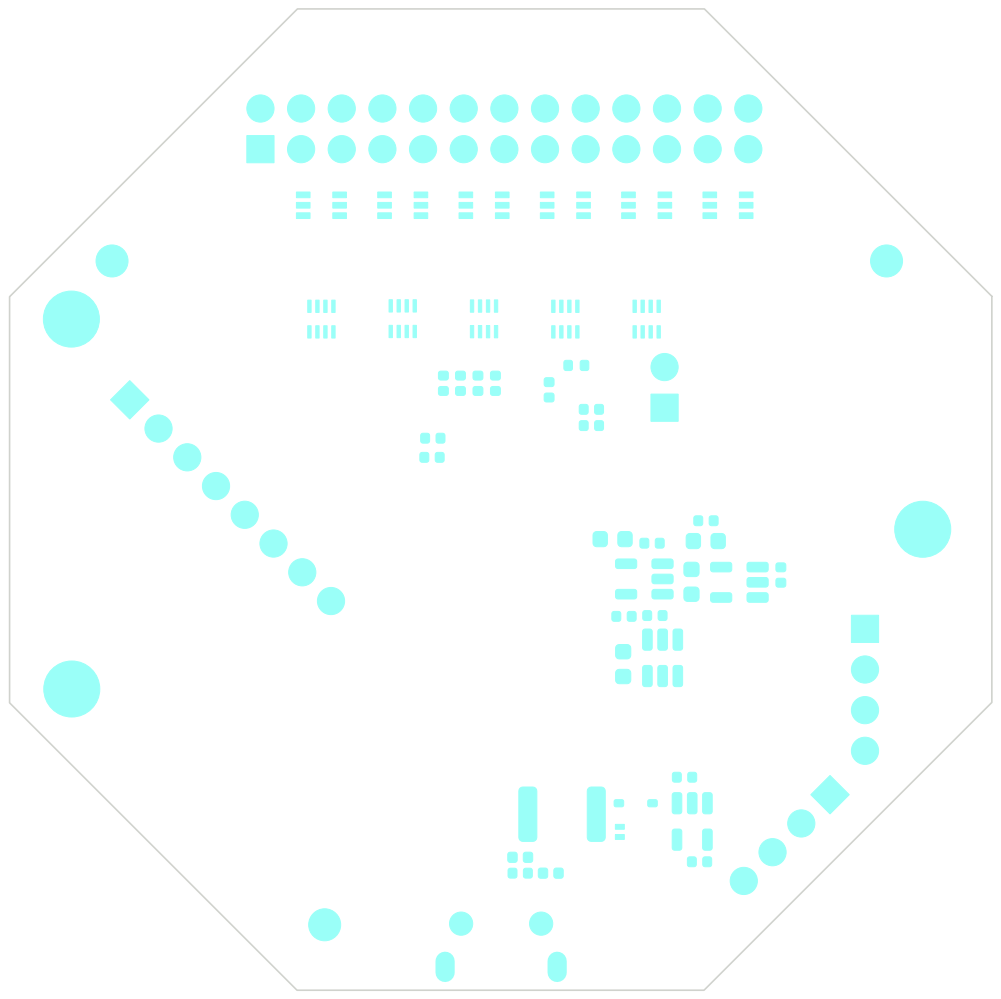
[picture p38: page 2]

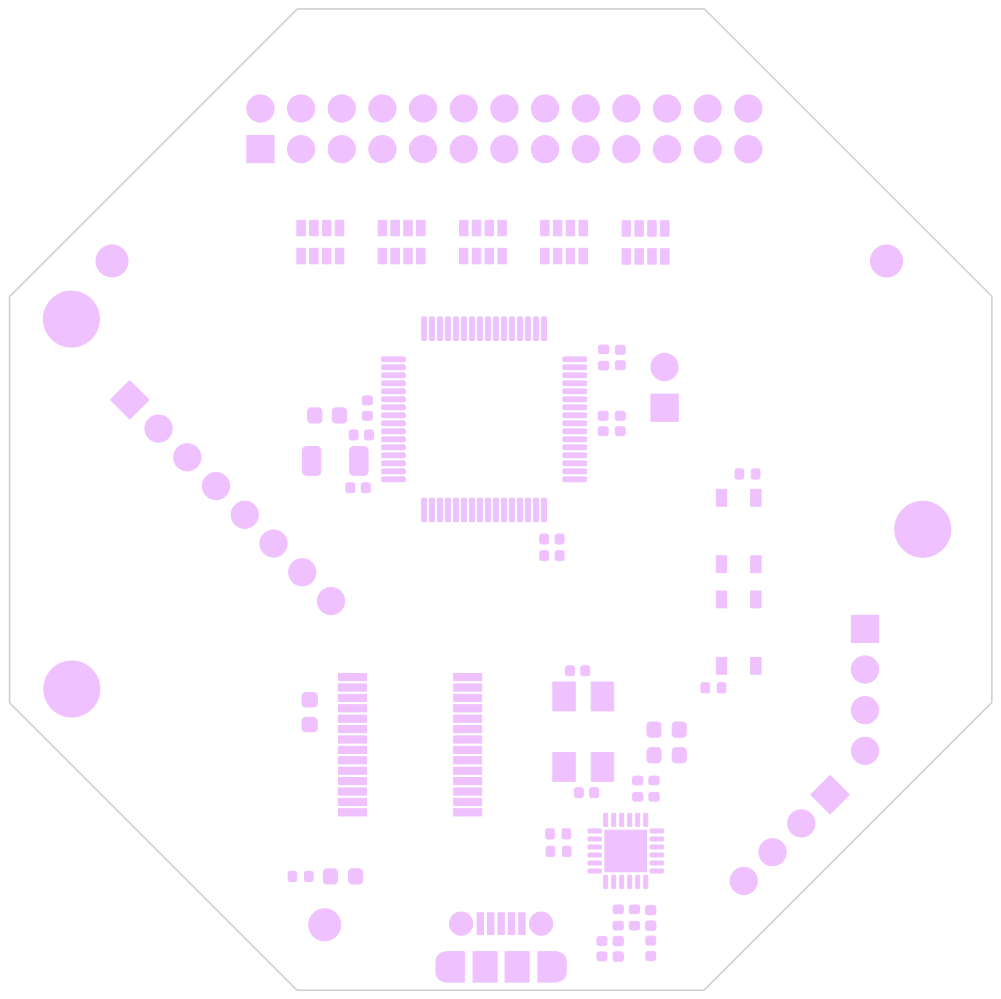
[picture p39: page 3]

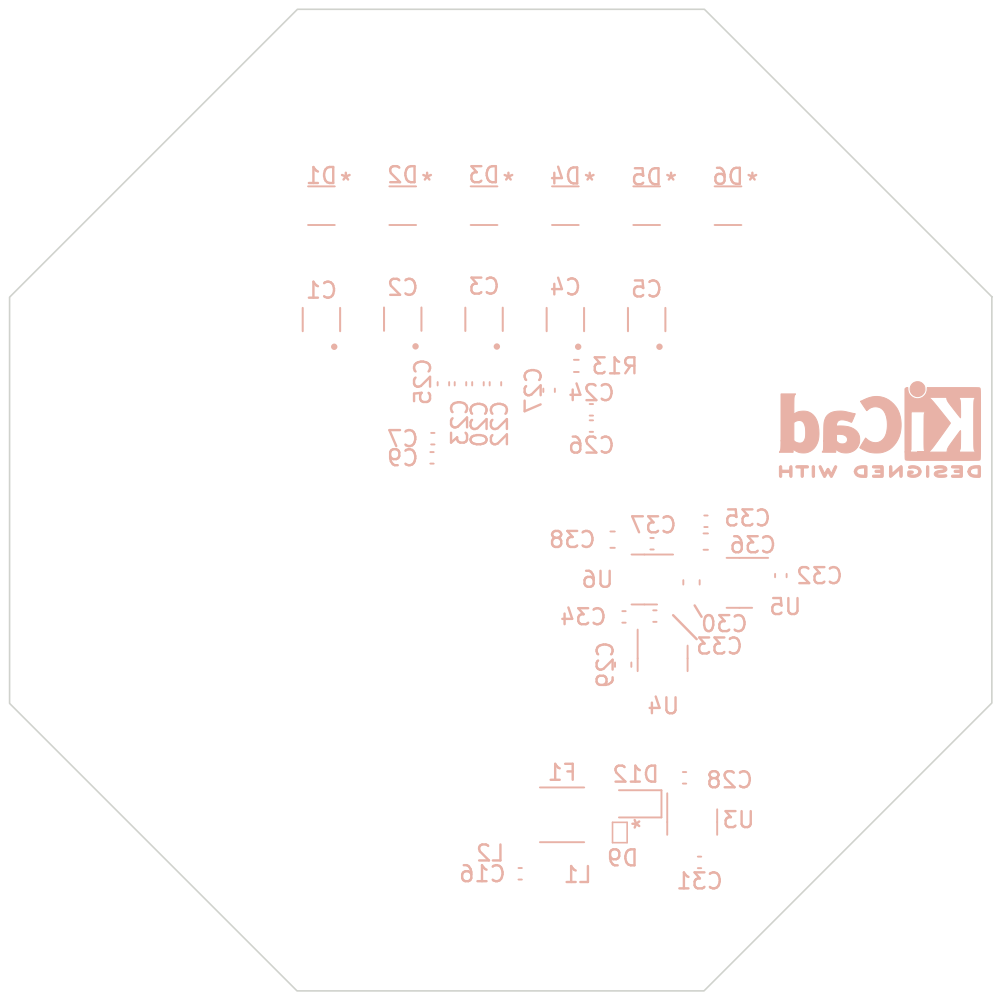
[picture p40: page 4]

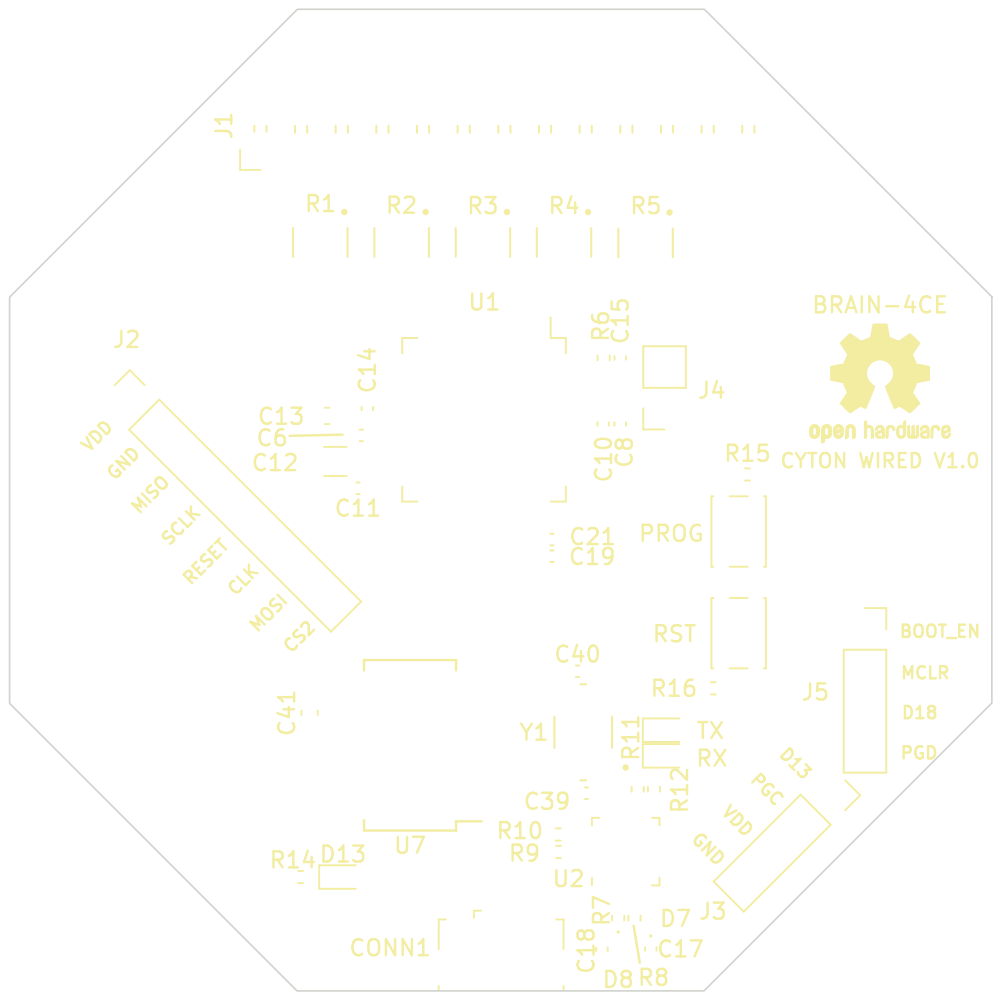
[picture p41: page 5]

CS2 D18 RX PGD CYTON WIRED V1.0 MISO

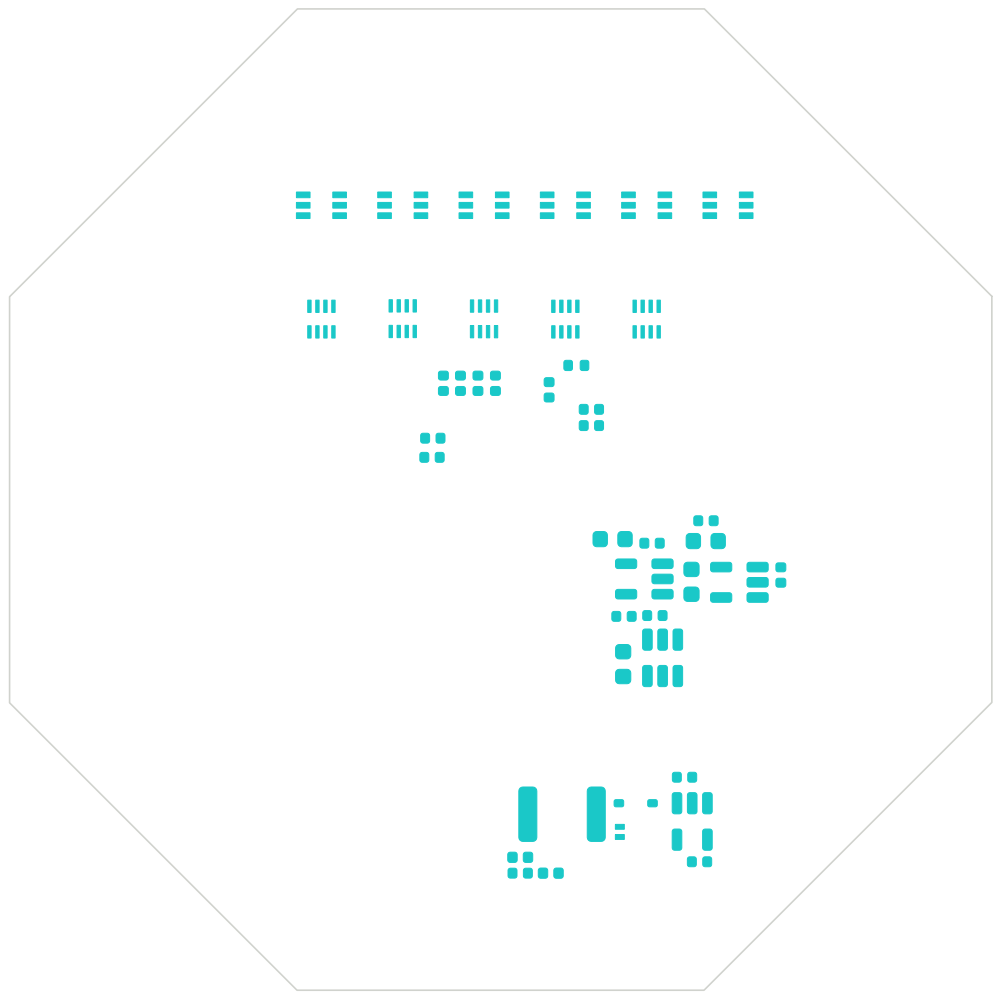
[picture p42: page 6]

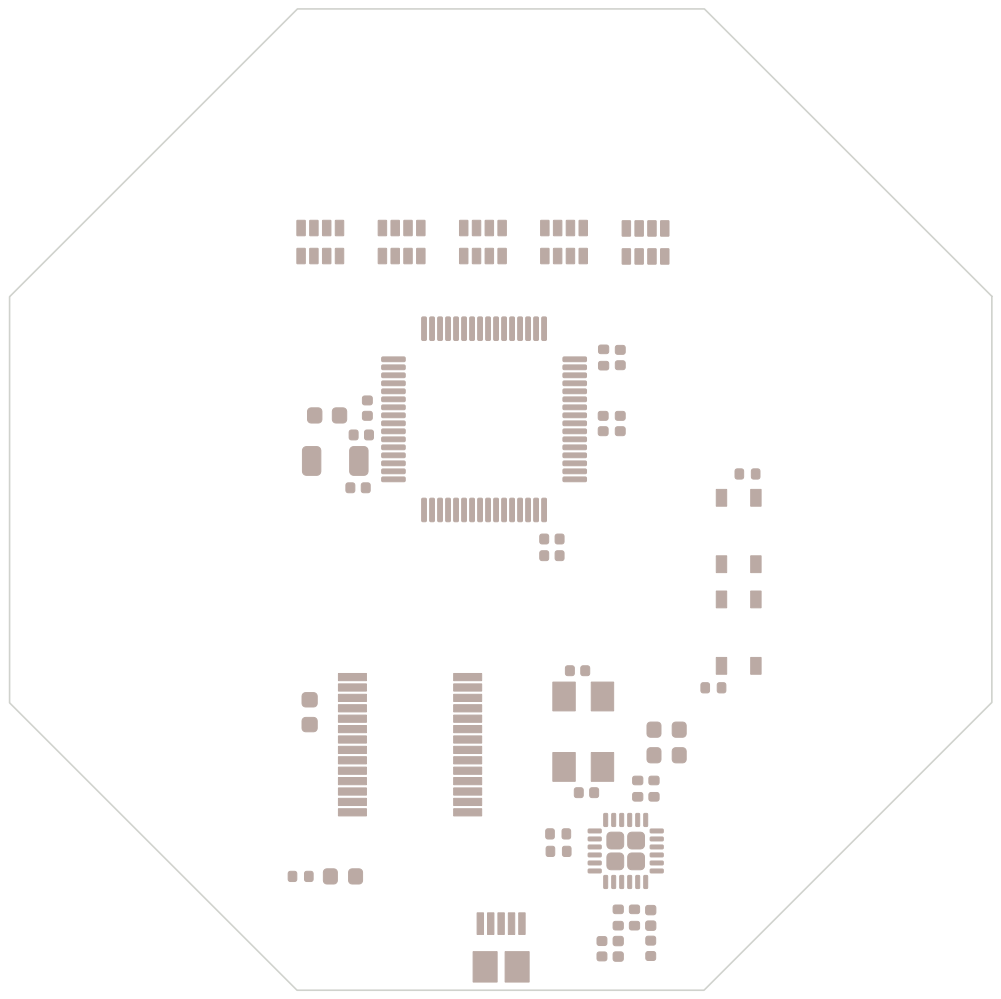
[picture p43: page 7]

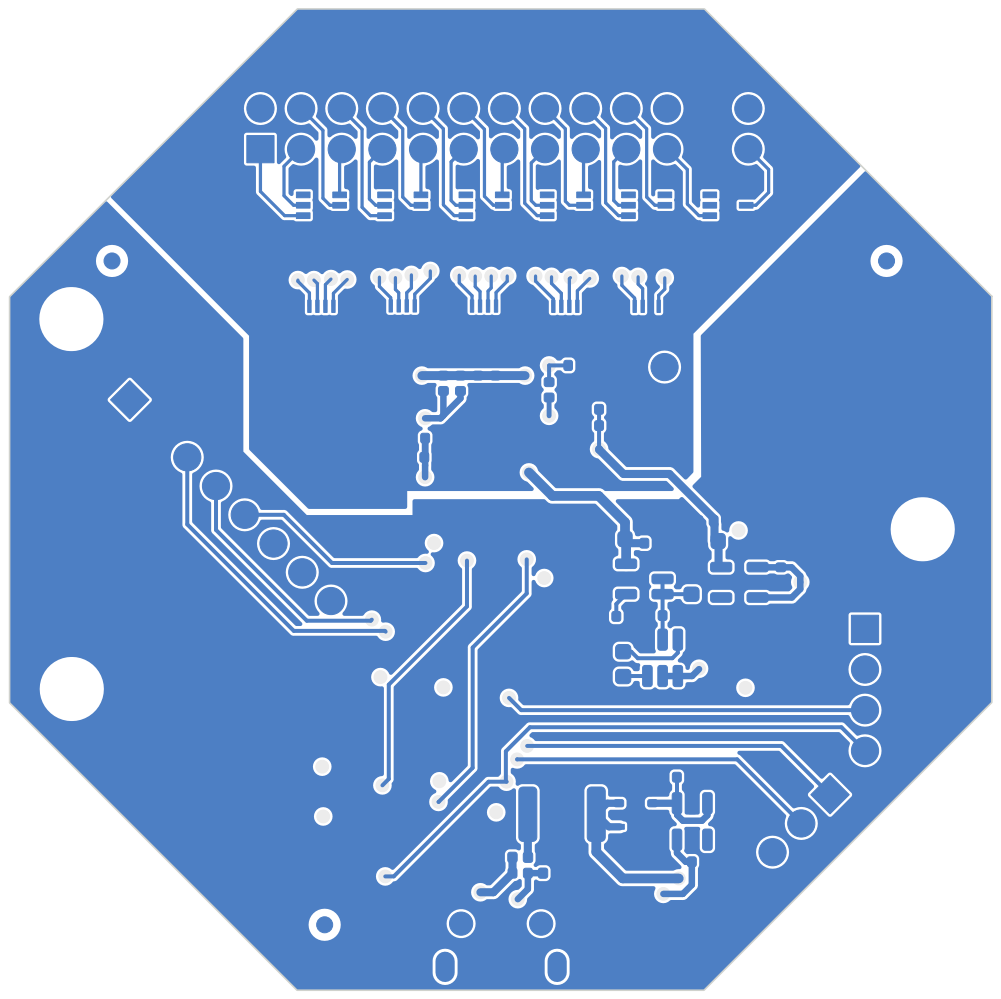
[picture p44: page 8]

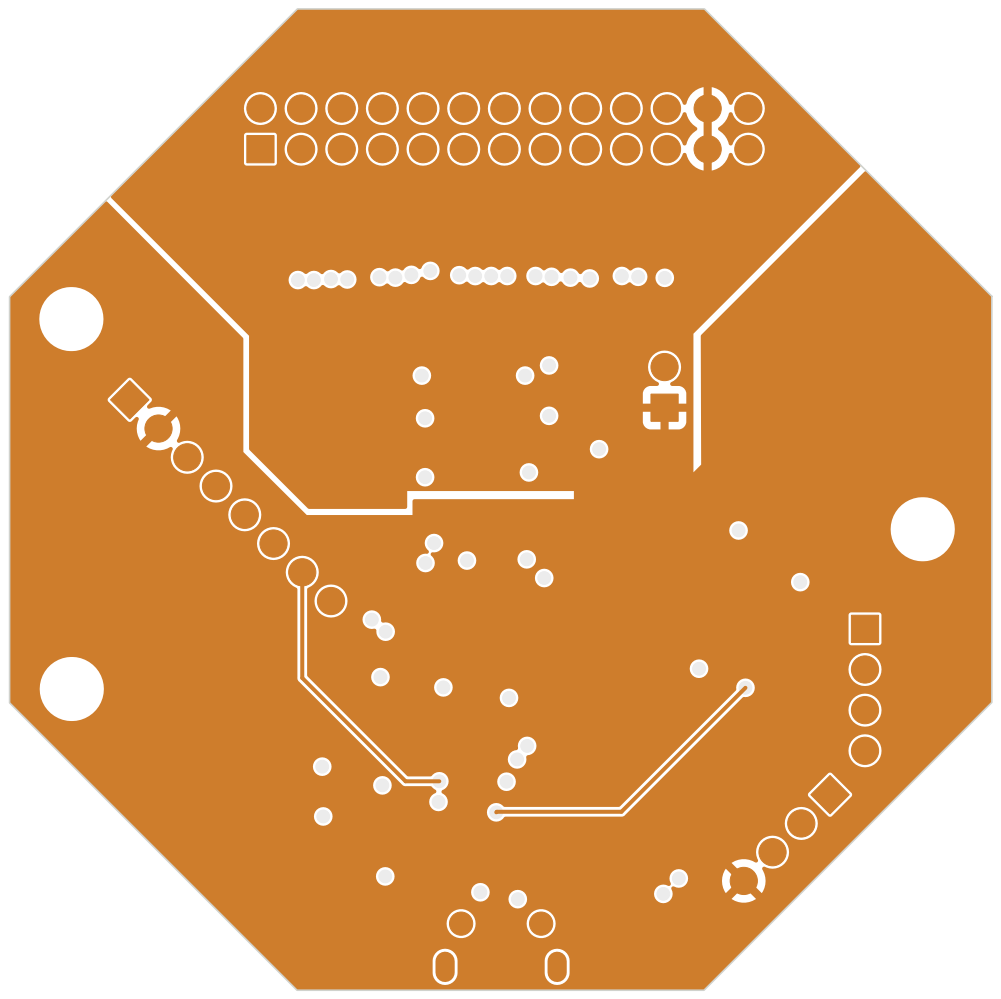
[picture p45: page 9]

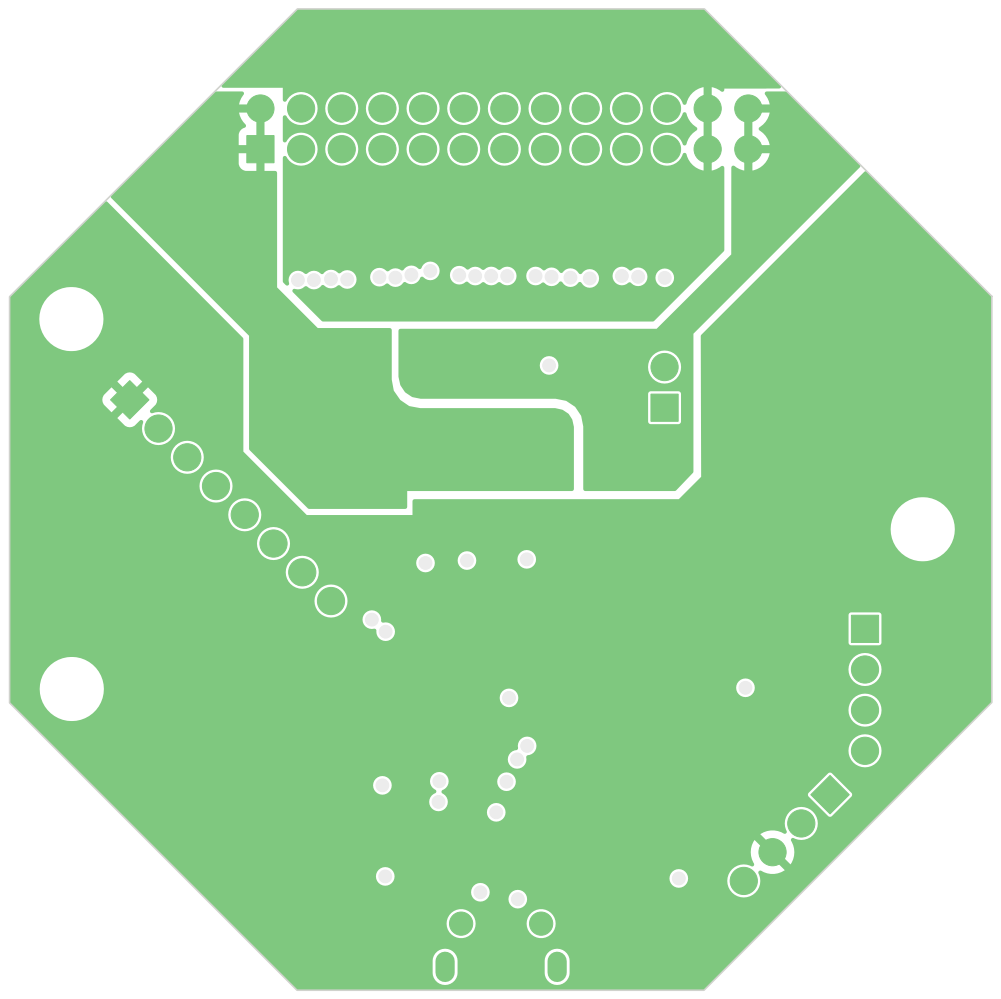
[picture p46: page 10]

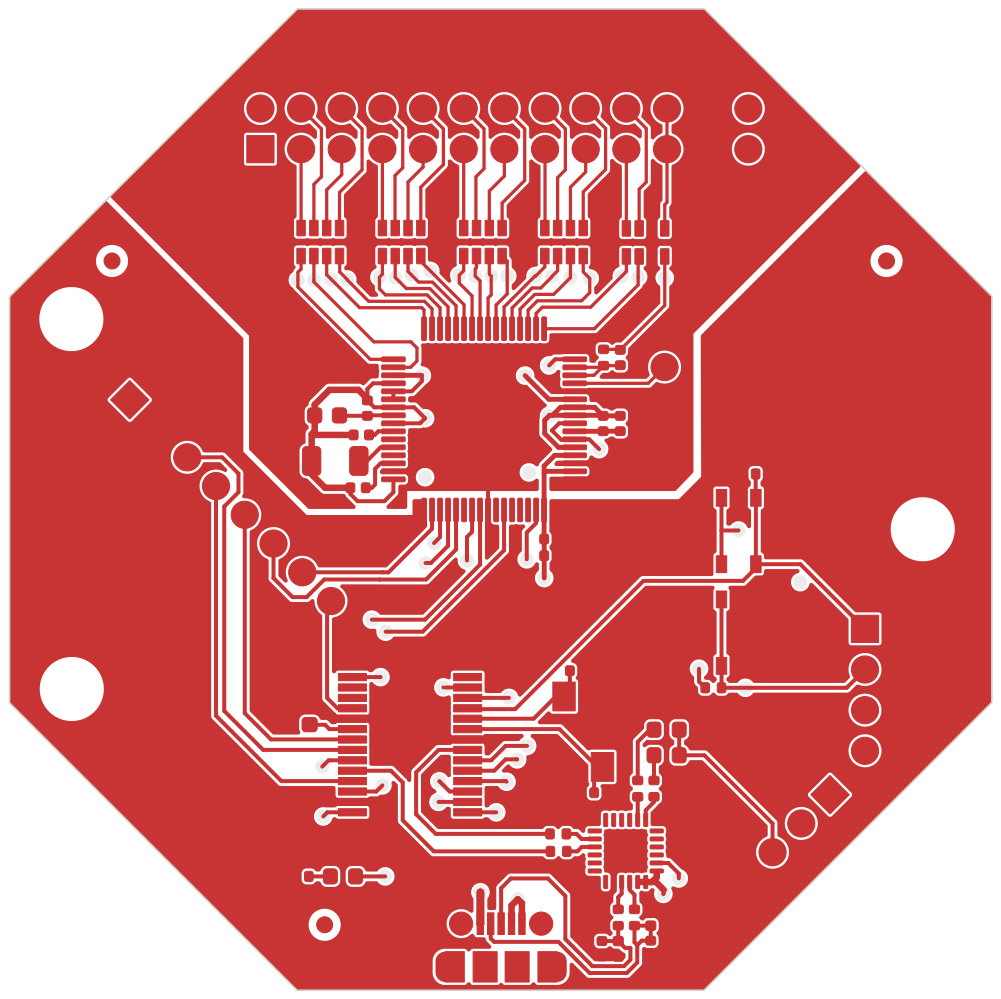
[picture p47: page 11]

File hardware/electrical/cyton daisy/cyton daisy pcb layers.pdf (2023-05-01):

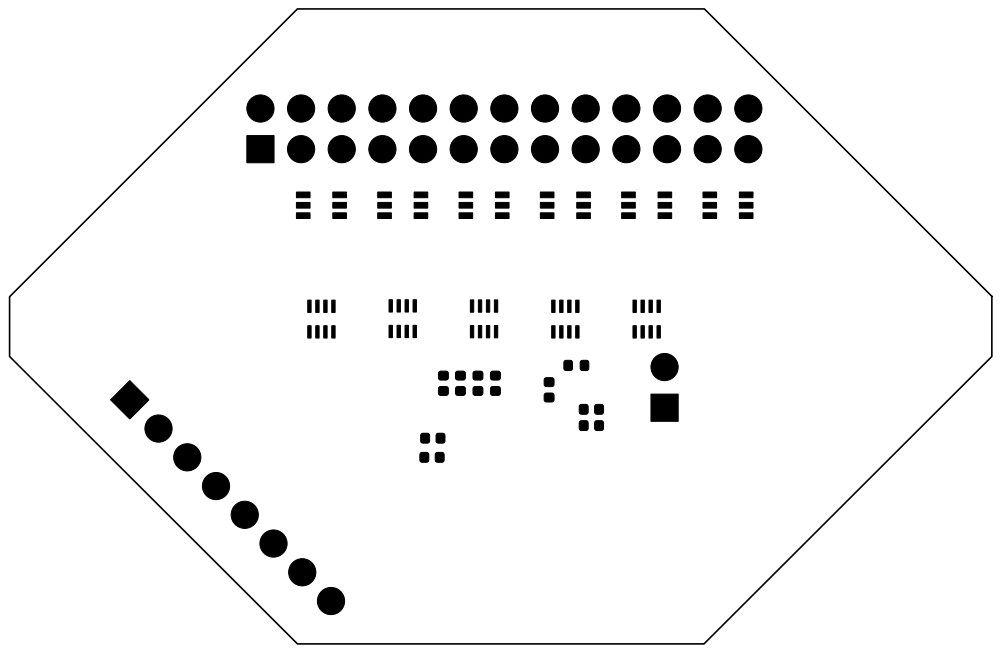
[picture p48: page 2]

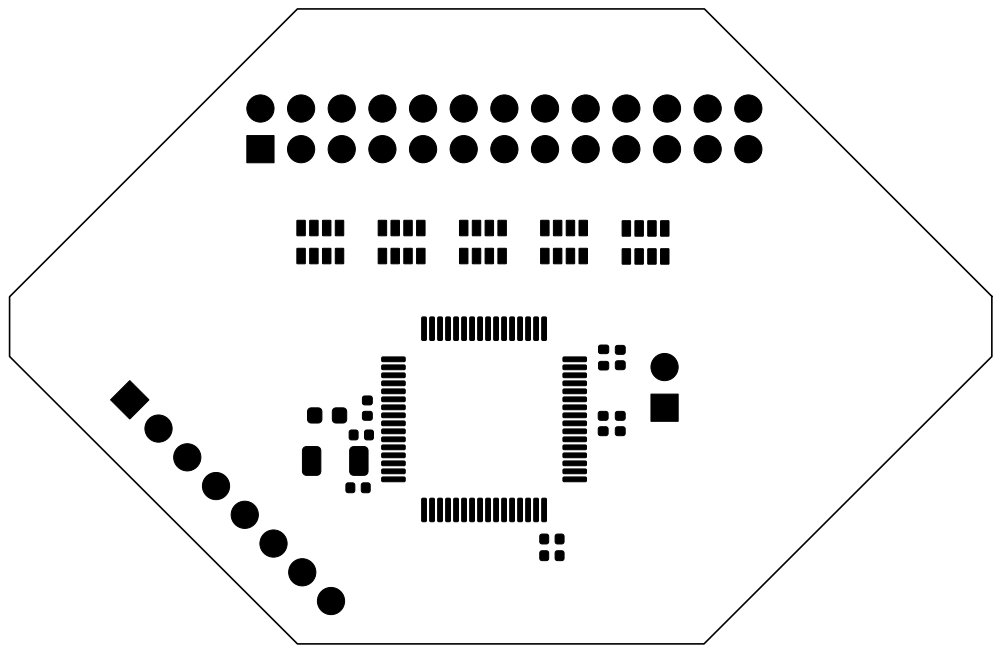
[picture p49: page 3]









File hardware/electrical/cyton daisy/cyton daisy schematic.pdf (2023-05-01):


Id: 1/2 Title: File: cyton daisy.kicad_sch Sheet: / Brain-4ce


Id: 2/2 Title: Daisy Functionality

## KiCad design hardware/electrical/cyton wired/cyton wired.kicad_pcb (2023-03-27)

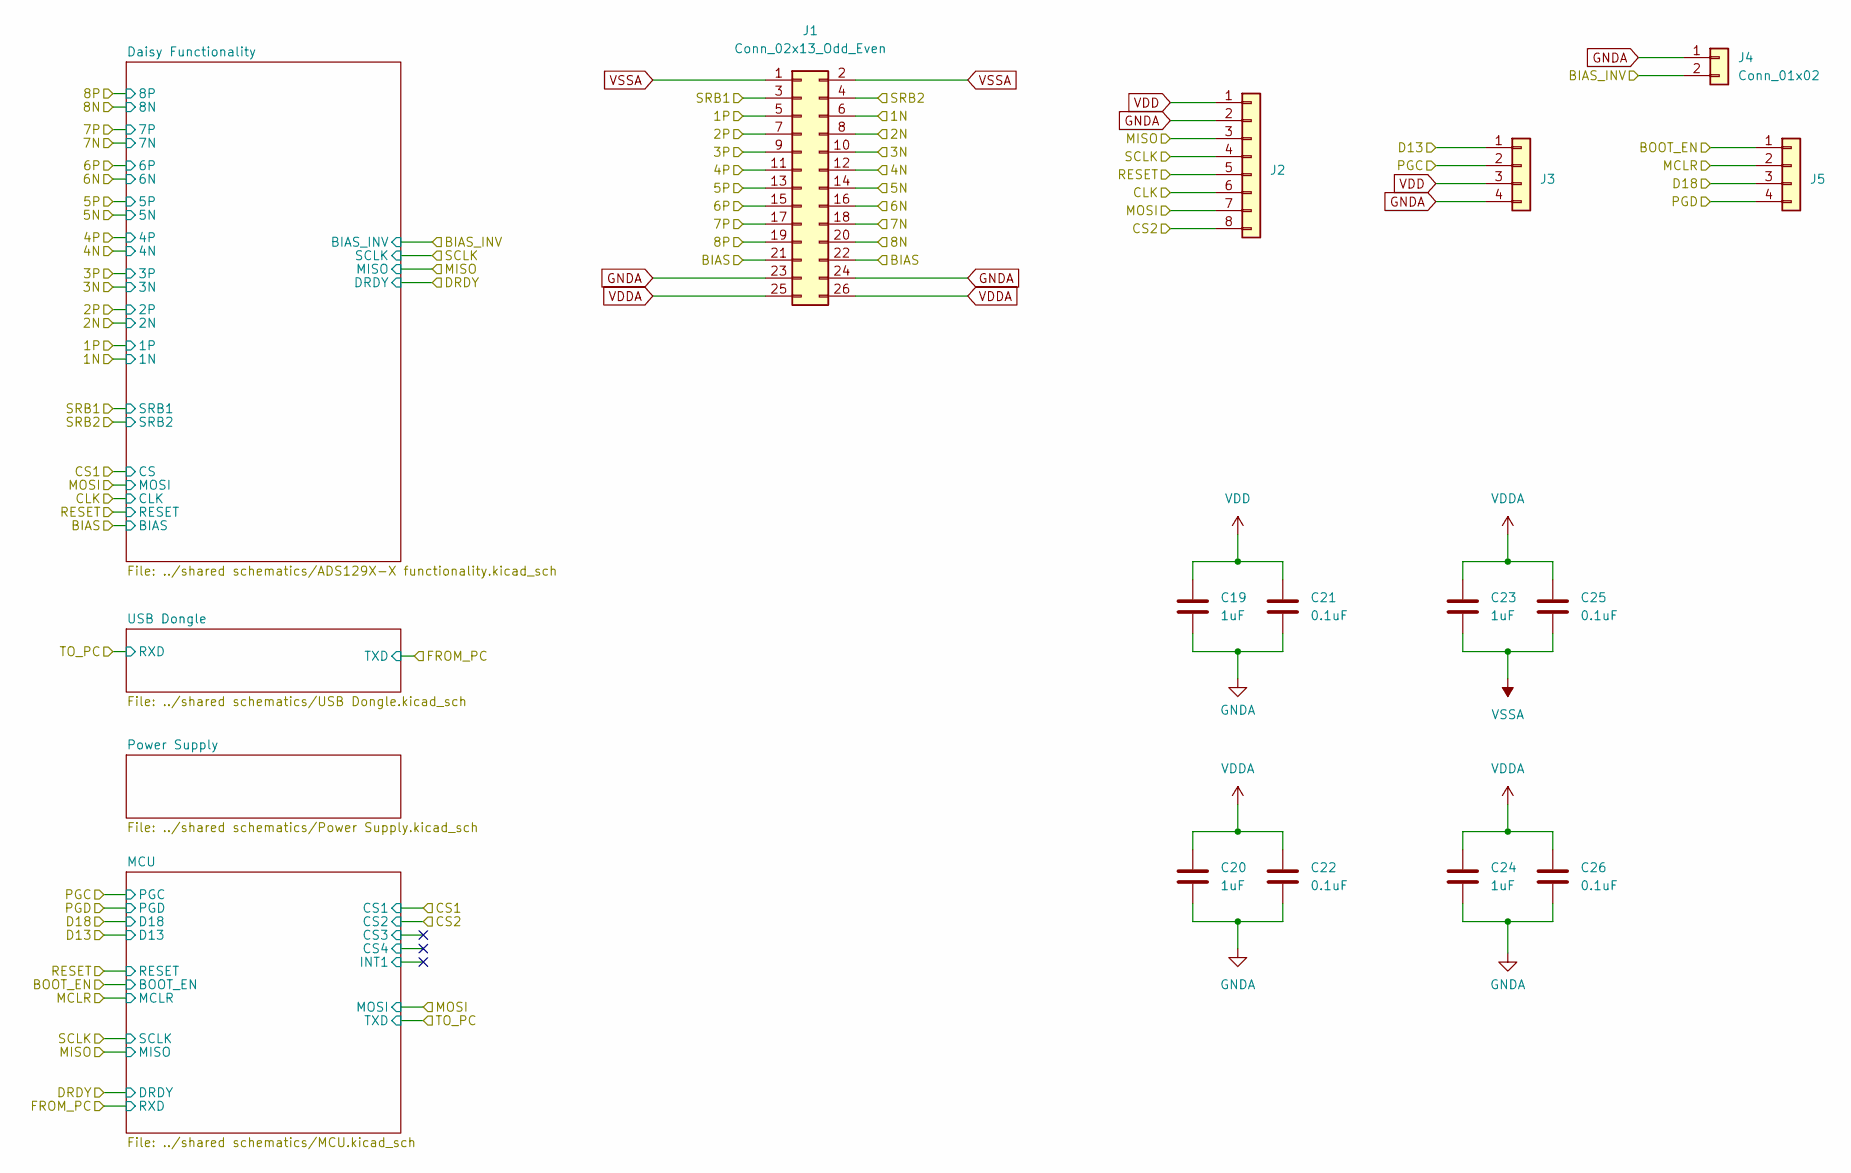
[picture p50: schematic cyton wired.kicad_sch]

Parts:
C19, C20, C23, C24: 1uF; C_0402_1005Metric
C21, C22, C25, C26: 0.1uF; C_0402_1005Metric
J1: Conn_02x13_Odd_Even; PinHeader_2x13_P2.54mm_Horizontal
J2: Conn_01x08; PinSocket_1x08_P2.54mm_Vertical
J3, J5: Conn_01x04; PinSocket_1x04_P2.54mm_Vertical
J4: Conn_01x02; PinSocket_1x02_P2.54mm_Vertical

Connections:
/1N: J1.6; also elsewhere on the board
/1P: J1.5; also elsewhere on the board
/2N: J1.8; also elsewhere on the board
/2P: J1.7; also elsewhere on the board
/3N: J1.10; also elsewhere on the board
/3P: J1.9; also elsewhere on the board
/4N: J1.12; also elsewhere on the board
/4P: J1.11; also elsewhere on the board
/5N: J1.14; also elsewhere on the board
/5P: J1.13; also elsewhere on the board
/6N: J1.16; also elsewhere on the board
/6P: J1.15; also elsewhere on the board
/7N: J1.18; also elsewhere on the board
/7P: J1.17; also elsewhere on the board
/8N: J1.20; also elsewhere on the board
/8P: J1.19; also elsewhere on the board
/BIAS: J1.21, J1.22; also elsewhere on the board
/BIAS_INV: J4.2; also elsewhere on the board
/BOOT_EN: J5.1; also elsewhere on the board
/CLK: J2.6; also elsewhere on the board
/CS2: J2.8; also elsewhere on the board
/D13: J3.1; also elsewhere on the board
/D18: J5.3; also elsewhere on the board
/MCLR: J5.2; also elsewhere on the board
/MISO: J2.3; also elsewhere on the board
/MOSI: J2.7; also elsewhere on the board
/PGC: J3.2; also elsewhere on the board
/PGD: J5.4; also elsewhere on the board
/RESET: J2.5; also elsewhere on the board
/SCLK: J2.4; also elsewhere on the board
/SRB1: J1.3; also elsewhere on the board
/SRB2: J1.4; also elsewhere on the board
GNDA: C19.2, C20.2, C21.2, C22.2, C24.2, C26.2, J1.23, J1.24, J2.2, J3.4, J4.1; also elsewhere on the board
VDD: C19.1, C21.1, J2.1, J3.3; also elsewhere on the board
VDDA: C20.1, C22.1, C23.1, C24.1, C25.1, C26.1, J1.25, J1.26; also elsewhere on the board
VSSA: C23.2, C25.2, J1.1, J1.2; also elsewhere on the board

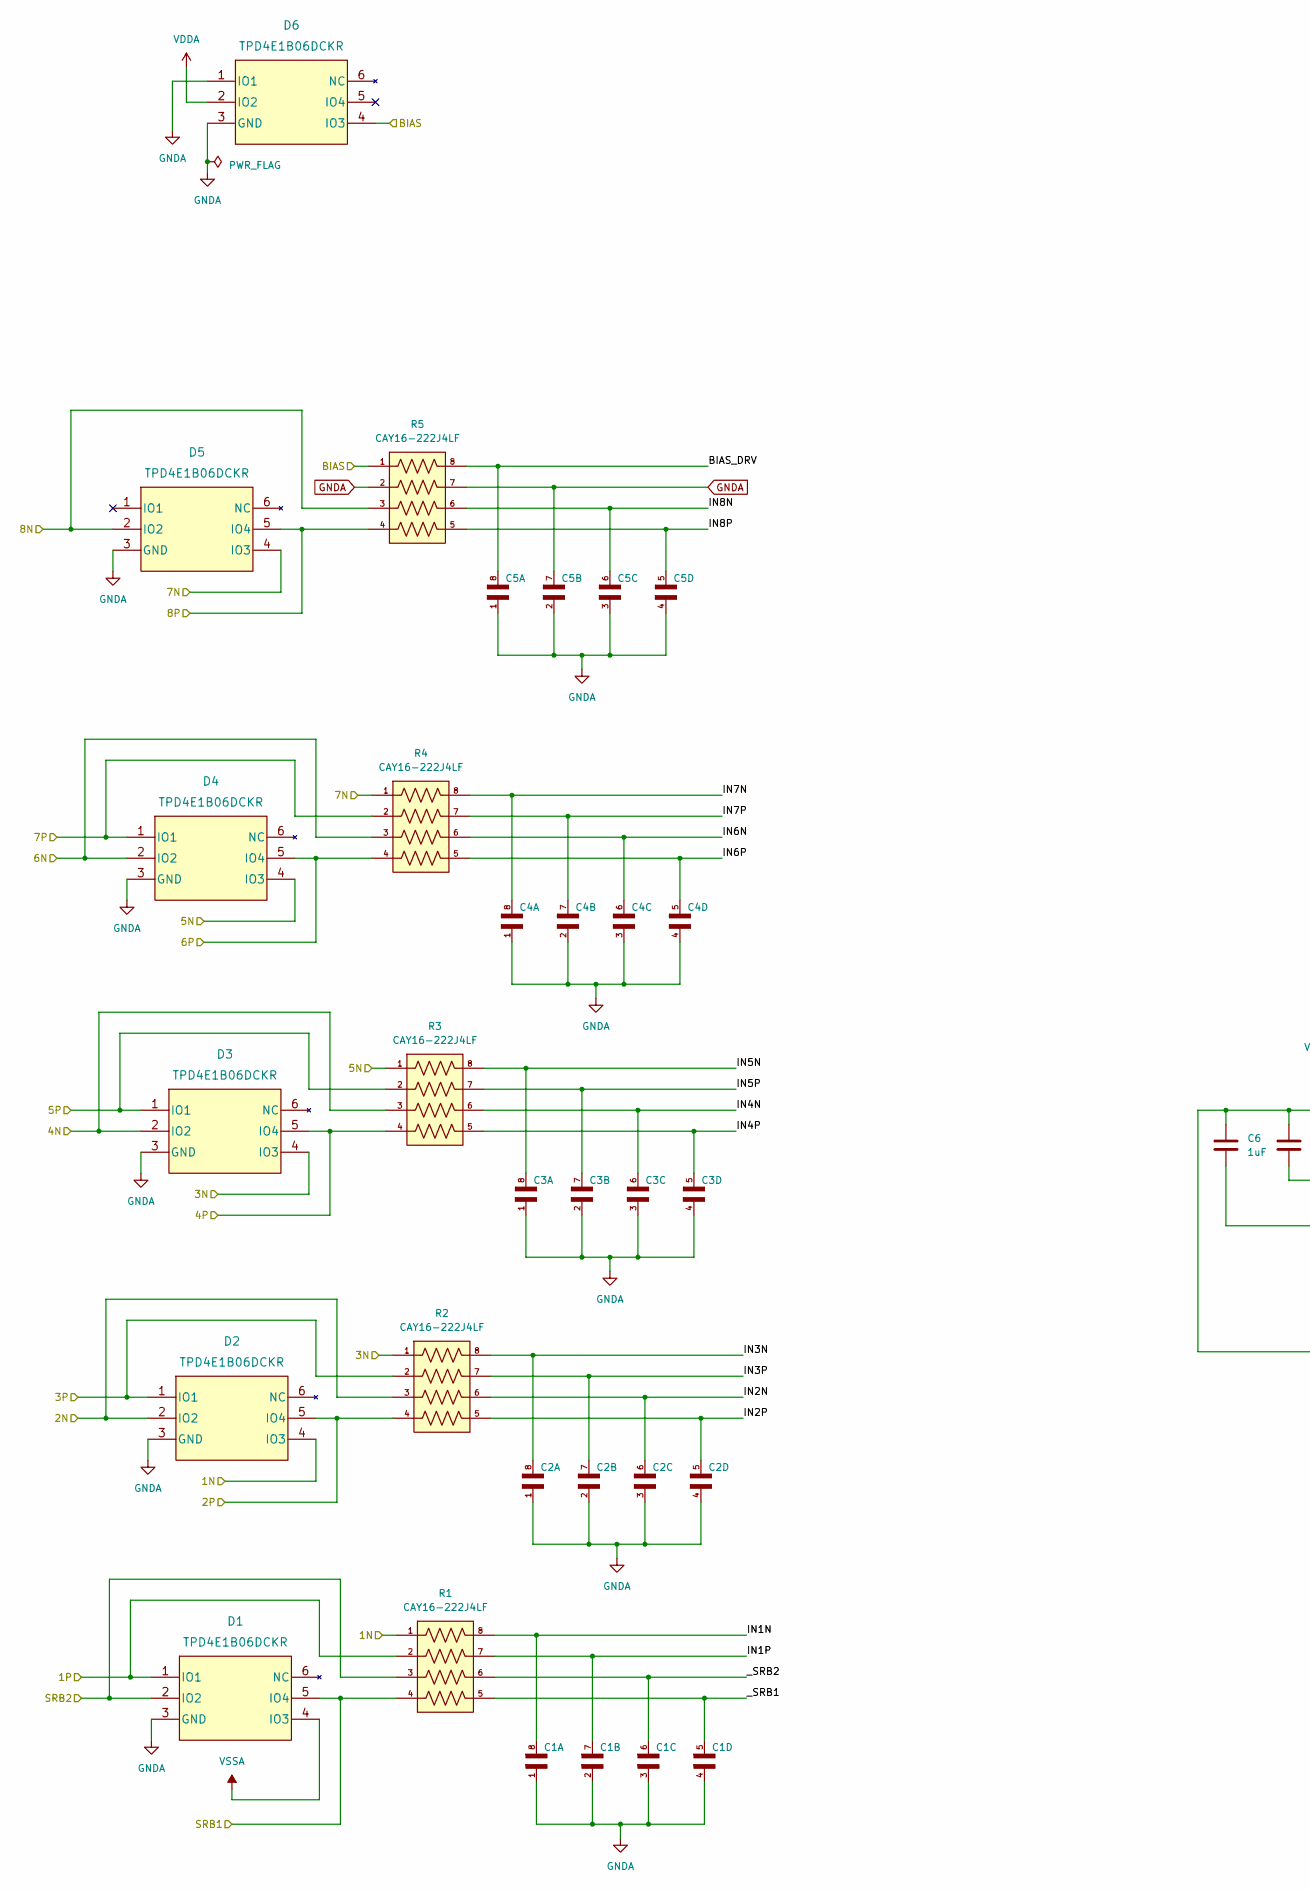
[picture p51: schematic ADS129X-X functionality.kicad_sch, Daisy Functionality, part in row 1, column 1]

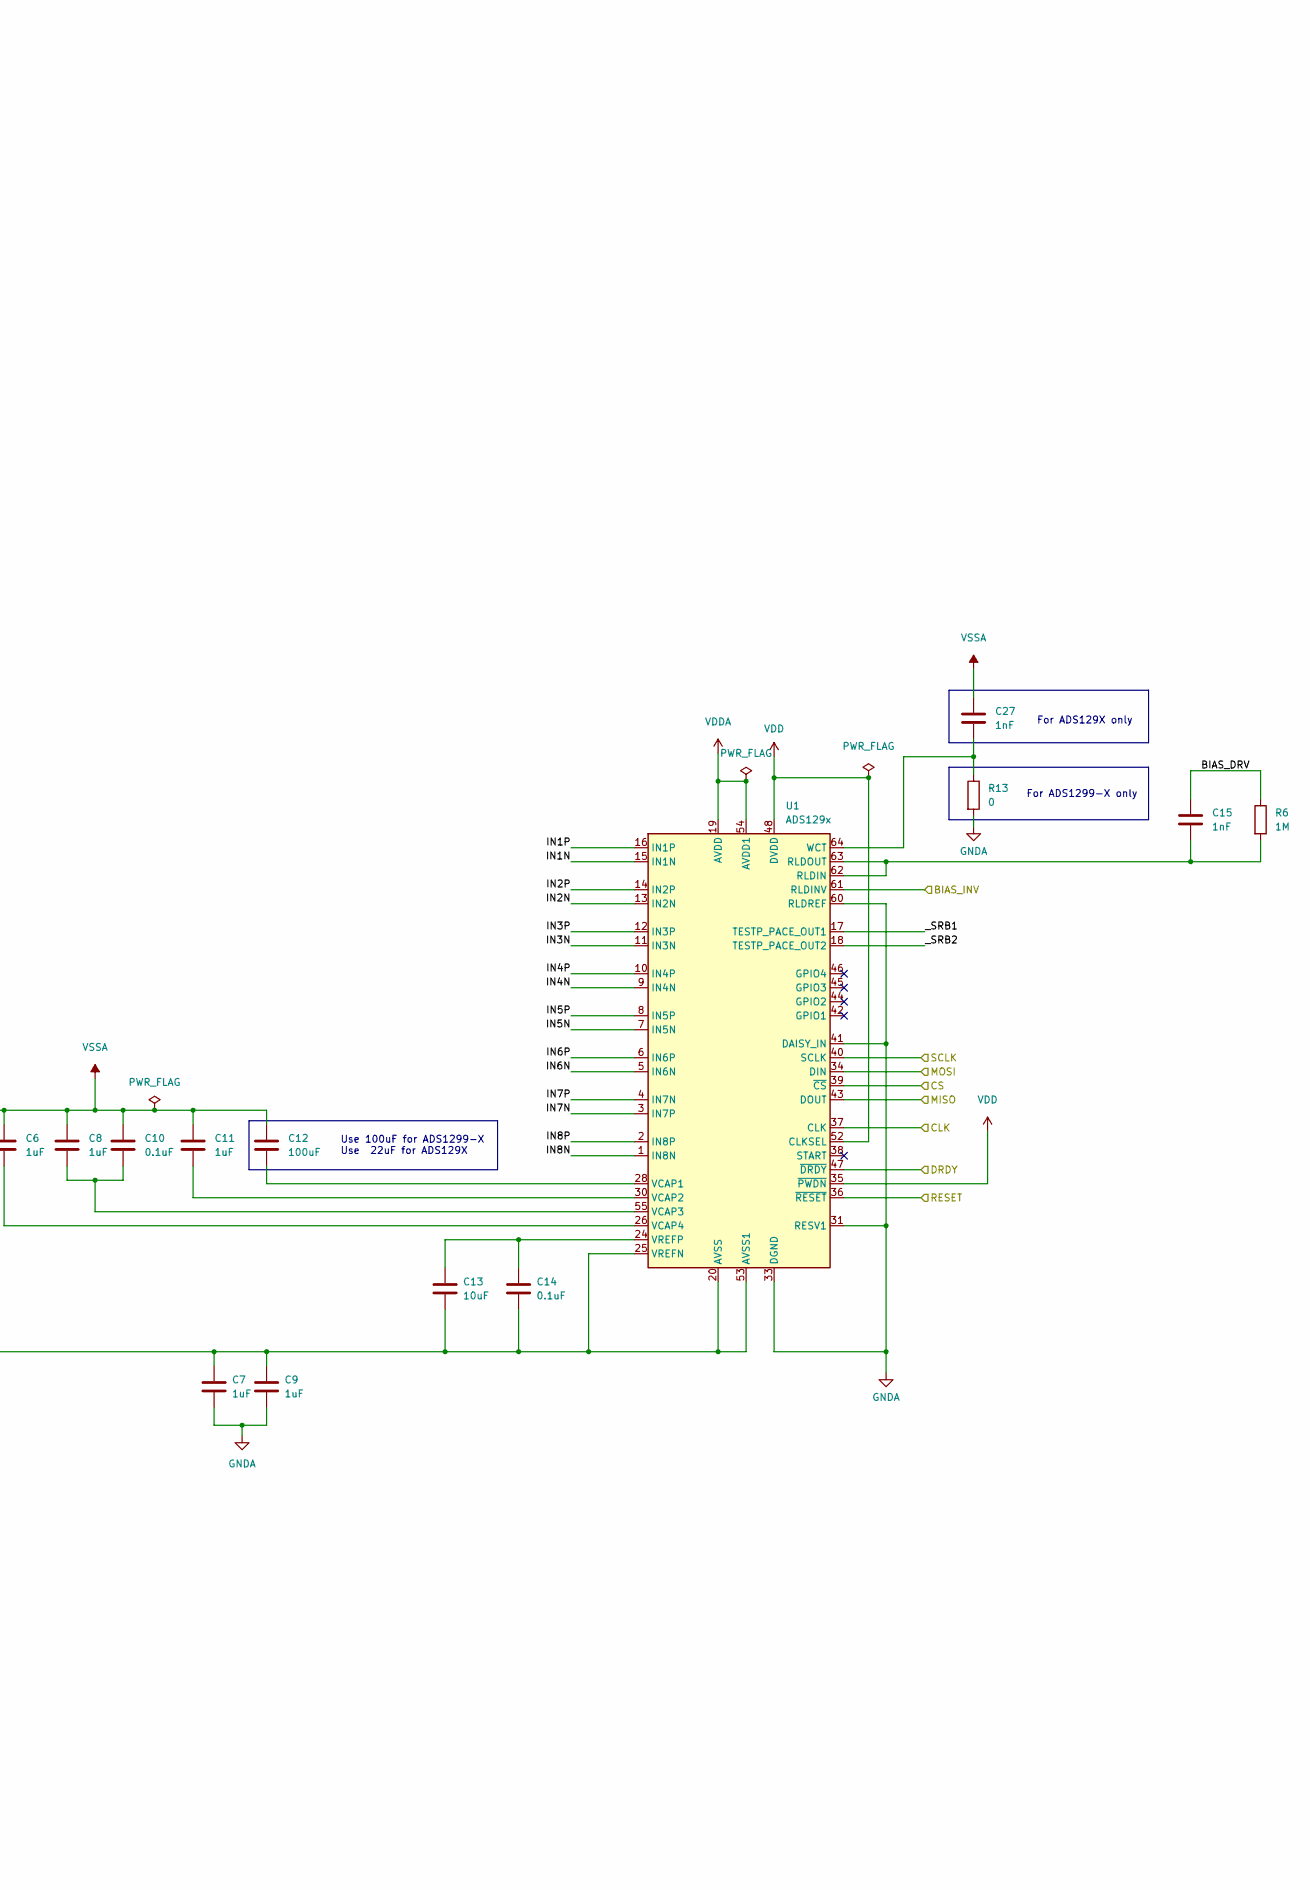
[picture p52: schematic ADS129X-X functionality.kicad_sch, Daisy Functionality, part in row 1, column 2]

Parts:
C1, C2, C3, C4, C5: CA0508KRX7R9BB102; CAPCAXE50P210X130X94-8N
C6, C7, C8, C9, C11: 1uF; C_0402_1005Metric
C10, C14: 0.1uF; C_0402_1005Metric
C12: 100uF; C_1206_3216Metric
C13: 10uF; C_0603_1608Metric
C15, C27: 1nF; C_0402_1005Metric
D1, D2, D3, D4, D5, D6: TPD4E1B06DCKR
R1, R2, R3, R4, R5: CAY16-222J4LF; RESCAF80P320X160X60-8N
R6: 1M; R_0402_1005Metric
R13: 0; R_0402_1005Metric
U1: ADS129x; TQFP-64_10x10mm_P0.5mm

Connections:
/1N: D2.4 (IO3), R1.1; also elsewhere on the board
/1P: D1.1 (IO1), R1.2; also elsewhere on the board
/2N: D2.2 (IO2), R2.3; also elsewhere on the board
/2P: D2.5 (IO4), R2.4; also elsewhere on the board
/3N: D3.4 (IO3), R2.1; also elsewhere on the board
/3P: D2.1 (IO1), R2.2; also elsewhere on the board
/4N: D3.2 (IO2), R3.3; also elsewhere on the board
/4P: D3.5 (IO4), R3.4; also elsewhere on the board
/5N: D4.4 (IO3), R3.1; also elsewhere on the board
/5P: D3.1 (IO1), R3.2; also elsewhere on the board
/6N: D4.2 (IO2), R4.3; also elsewhere on the board
/6P: D4.5 (IO4), R4.4; also elsewhere on the board
/7N: D5.4 (IO3), R4.1; also elsewhere on the board
/7P: D4.1 (IO1), R4.2; also elsewhere on the board
/8N: D5.2 (IO2), R5.3; also elsewhere on the board
/8P: D5.5 (IO4), R5.4; also elsewhere on the board
/BIAS: D6.4 (IO3), R5.1; also elsewhere on the board
/BIAS_INV: U1.61 (RLDINV); also elsewhere on the board
/CLK: U1.37 (CLK); also elsewhere on the board
/CS1: U1.39 (~CS); also elsewhere on the board
/DRDY: U1.47 (~DRDY); also elsewhere on the board
/Daisy Functionality/BIAS_DRV: C5.8, C15.1, R5.8, R6.1
/Daisy Functionality/IN1N: C1.8, R1.8, U1.15 (IN1N)
/Daisy Functionality/IN1P: C1.7, R1.7, U1.16 (IN1P)
/Daisy Functionality/IN2N: C2.6, R2.6, U1.13 (IN2N)
/Daisy Functionality/IN2P: C2.5, R2.5, U1.14 (IN2P)
/Daisy Functionality/IN3N: C2.8, R2.8, U1.11 (IN3N)
/Daisy Functionality/IN3P: C2.7, R2.7, U1.12 (IN3P)
/Daisy Functionality/IN4N: C3.6, R3.6, U1.9 (IN4N)
/Daisy Functionality/IN4P: C3.5, R3.5, U1.10 (IN4P)
/Daisy Functionality/IN5N: C3.8, R3.8, U1.7 (IN5N)
/Daisy Functionality/IN5P: C3.7, R3.7, U1.8 (IN5P)
/Daisy Functionality/IN6N: C4.6, R4.6, U1.5 (IN6N)
/Daisy Functionality/IN6P: C4.5, R4.5, U1.6 (IN6P)
/Daisy Functionality/IN7N: C4.8, R4.8, U1.3 (IN7P)
/Daisy Functionality/IN7P: C4.7, R4.7, U1.4 (IN7N)
/Daisy Functionality/IN8N: C5.6, R5.6, U1.1 (IN8N)
/Daisy Functionality/IN8P: C5.5, R5.5, U1.2 (IN8P)
/Daisy Functionality/_SRB1: C1.5, R1.5, U1.17 (TESTP_PACE_OUT1)
/Daisy Functionality/_SRB2: C1.6, R1.6, U1.18 (TESTP_PACE_OUT2)
/MISO: U1.43 (DOUT); also elsewhere on the board
/MOSI: U1.34 (DIN); also elsewhere on the board
/RESET: U1.36 (~RESET); also elsewhere on the board
/SCLK: U1.40 (SCLK); also elsewhere on the board
/SRB1: D1.5 (IO4), R1.4; also elsewhere on the board
/SRB2: D1.2 (IO2), R1.3; also elsewhere on the board
GNDA: C1.1, C1.2, C1.3, C1.4, C2.1, C2.2, C2.3, C2.4, C3.1, C3.2, C3.3, C3.4, C4.1, C4.2, C4.3, C4.4, C5.1, C5.2, C5.3, C5.4, C5.7, C7.2, C9.2, D1.3 (GND), D2.3 (GND), D3.3 (GND), D4.3 (GND), D5.3 (GND), D6.1 (IO1), D6.3 (GND), R5.2, R5.7, R13.2, U1.31 (RESV1), U1.33 (DGND), U1.41 (DAISY_IN), U1.49 (DGND), U1.51 (DGND), U1.60 (RLDREF); also elsewhere on the board
unnamed: C15.2, R6.2, U1.62 (RLDIN), U1.63 (RLDOUT)
unnamed: C12.2, U1.28 (VCAP1)
unnamed: C11.2, U1.30 (VCAP2)
unnamed: C8.2, C10.2, U1.55 (VCAP3)
unnamed: C6.2, U1.26 (VCAP4)
unnamed: C13.1, C14.1, U1.24 (VREFP)
unnamed: C27.2, R13.1, U1.64 (WCT)
VDD: U1.35 (~PWDN), U1.48 (DVDD), U1.50 (DVDD), U1.52 (CLKSEL); also elsewhere on the board
VDDA: D6.2 (IO2), U1.19 (AVDD), U1.21 (AVDD), U1.22 (AVDD), U1.54 (AVDD1), U1.56 (AVDD), U1.59 (AVDD); also elsewhere on the board
VSSA: C6.1, C7.1, C8.1, C9.1, C10.1, C11.1, C12.1, C13.2, C14.2, C27.1, D1.4 (IO3), U1.20 (AVSS), U1.23 (AVSS), U1.25 (VREFN), U1.32 (AVSS), U1.53 (AVSS1), U1.57 (AVSS), U1.58 (AVSS); also elsewhere on the board

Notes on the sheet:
For ADS1299-X only
Use 100uF for ADS1299-X Use 22uF for ADS129X
For ADS129X only

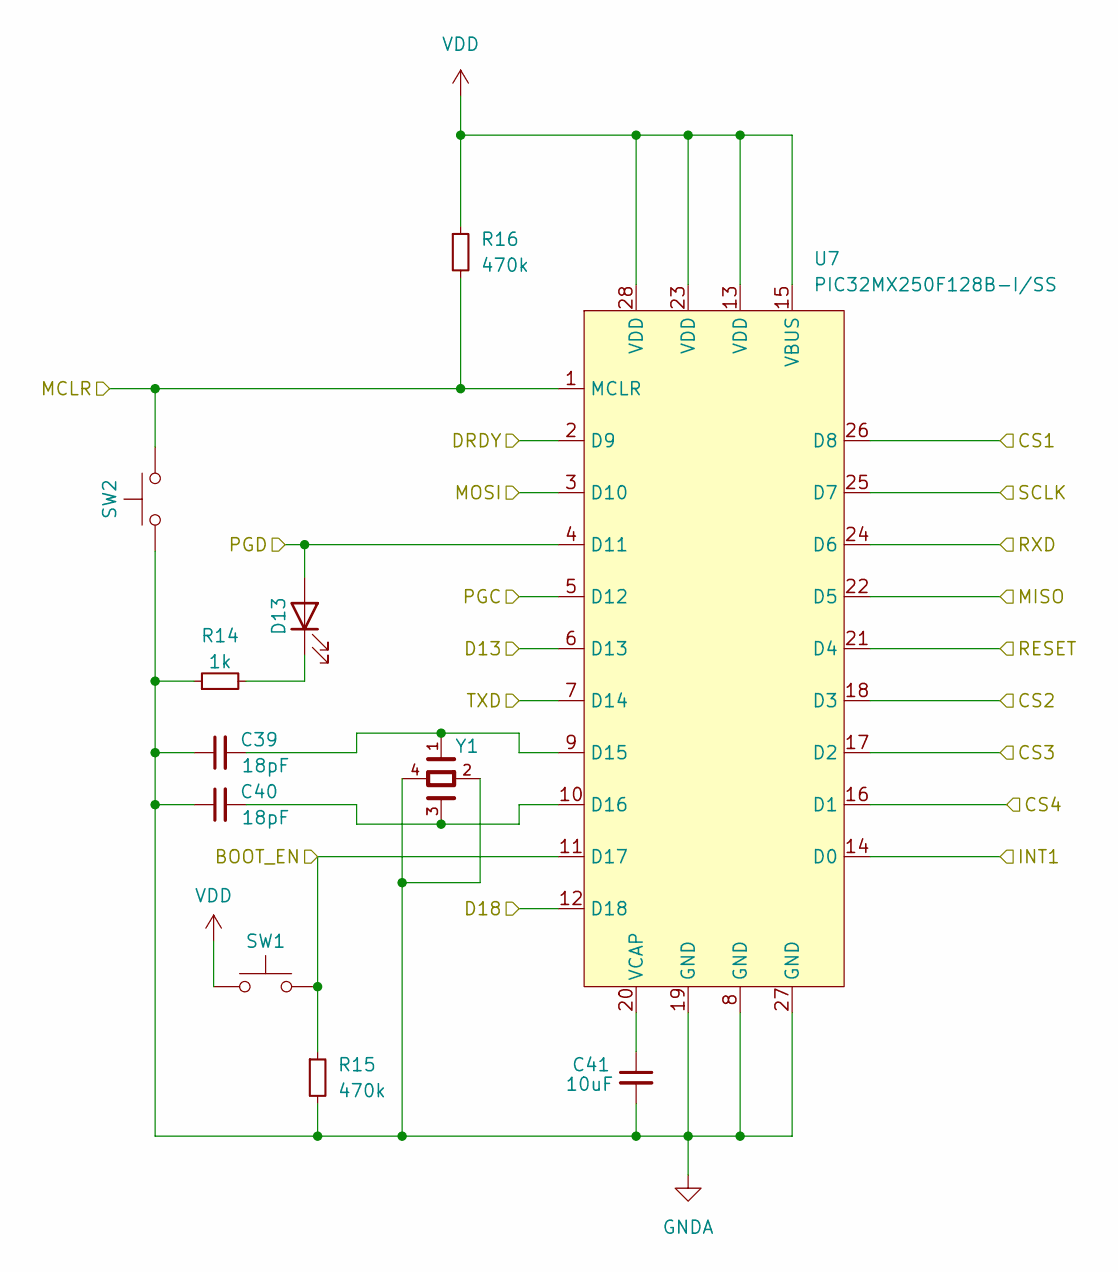
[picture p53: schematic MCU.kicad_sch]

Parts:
C39, C40: 18pF; C_0402_1005Metric
C41: 10uF; C_0603_1608Metric
D13: LED; LED_0603_1608Metric
R14: 1k; R_0402_1005Metric
R15, R16: 470k; R_0402_1005Metric
SW1, SW2: SW_Push; SW_SPST_PTS810
U7: PIC32MX250F128B-I/SS; SSOP-28_5.3x10.2mm_P0.65mm
Y1: ABMM2-8.000MHZ-E2-T; XTAL_ABMM2-8.000MHZ-E2-T; PARTREV 01.18.13

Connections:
/BOOT_EN: R15.1, SW1.2, U7.11 (D17); also elsewhere on the board
/CS1: U7.26 (D8); also elsewhere on the board
/CS2: U7.18 (D3); also elsewhere on the board
/D13: U7.6 (D13); also elsewhere on the board
/D18: U7.12 (D18); also elsewhere on the board
/DRDY: U7.2 (D9); also elsewhere on the board
/FROM_PC: U7.24 (D6); also elsewhere on the board
/MCLR: R16.2, SW2.2, U7.1 (MCLR); also elsewhere on the board
/MCU/CS3: U7.17 (D2)
/MCU/CS4: U7.16 (D1)
/MCU/INT1: U7.14 (D0)
/MISO: U7.22 (D5); also elsewhere on the board
/MOSI: U7.3 (D10); also elsewhere on the board
/PGC: U7.5 (D12); also elsewhere on the board
/PGD: D13.2 (A), U7.4 (D11); also elsewhere on the board
/RESET: U7.21 (D4); also elsewhere on the board
/SCLK: U7.25 (D7); also elsewhere on the board
/TO_PC: U7.7 (D14); also elsewhere on the board
GNDA: C39.1, C40.1, C41.2, R14.1, R15.2, SW2.1, U7.8 (GND), U7.19 (GND), U7.27 (GND), Y1.2, Y1.4; also elsewhere on the board
unnamed: D13.1 (K), R14.2
unnamed: C39.2, U7.9 (D15), Y1.1
unnamed: C40.2, U7.10 (D16), Y1.3
unnamed: C41.1, U7.20 (VCAP)
VDD: R16.1, SW1.1, U7.13 (VDD), U7.15 (VBUS), U7.23 (VDD), U7.28 (VDD); also elsewhere on the board

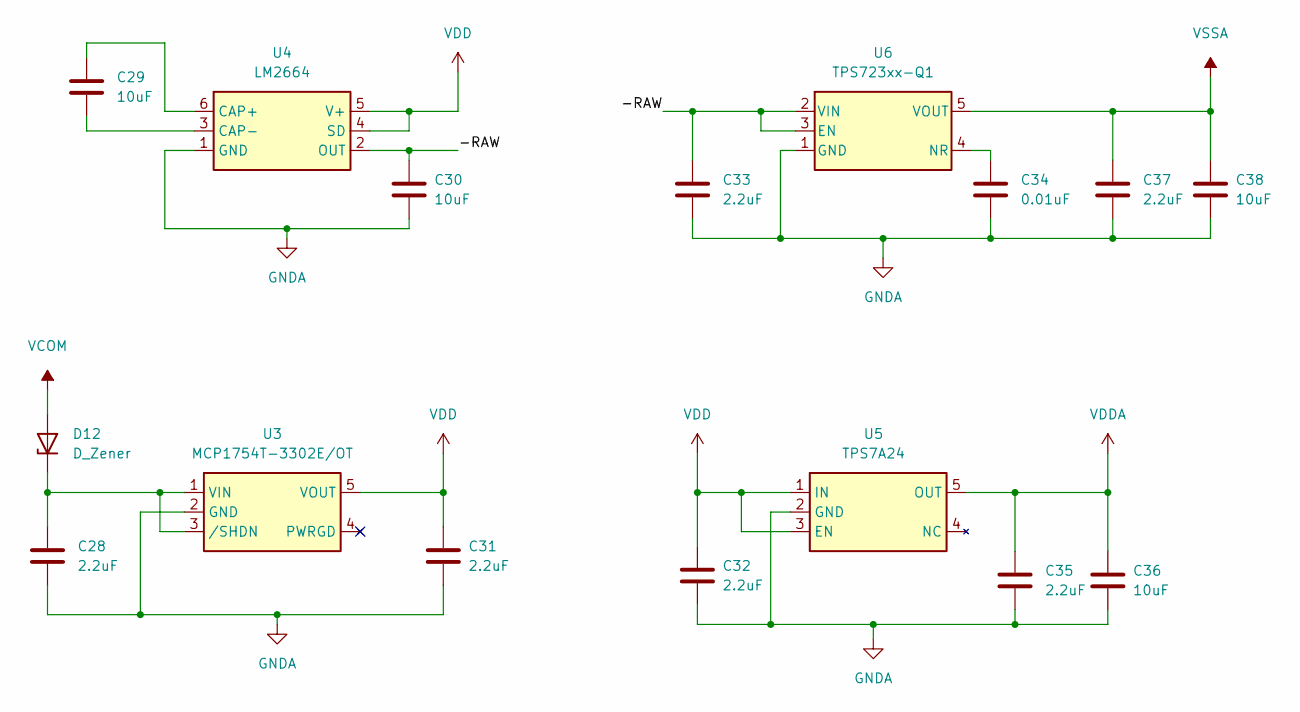
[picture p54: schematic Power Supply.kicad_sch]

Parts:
C28, C31, C32, C33, C35, C37: 2.2uF; C_0402_1005Metric
C29, C30, C36, C38: 10uF; C_0603_1608Metric
C34: 0.01uF; C_0402_1005Metric
D12: D_Zener; D_SOD-323
U3: MCP1754T-3302E/OT; SOT-23-5
U4: LM2664; SOT-23-6
U5: TPS7A24; SOT-23-5
U6: TPS723xx-Q1; SOT-23-5

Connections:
/Power Supply/-RAW: C30.1, C33.1, U4.2 (OUT), U6.2 (VIN), U6.3 (EN)
GNDA: C28.2, C30.2, C31.2, C32.2, C33.2, C34.2, C35.2, C36.2, C37.2, C38.2, U3.2 (GND), U4.1 (GND), U5.2 (GND), U6.1 (GND); also elsewhere on the board
unnamed: C28.1, D12.1 (K), U3.1 (VIN), U3.3 (/SHDN)
unnamed: C29.1, U4.6 (CAP+)
unnamed: C29.2, U4.3 (CAP-)
unnamed: C34.1, U6.4 (NR)
VCOM: D12.2 (A); also elsewhere on the board
VDD: C31.1, C32.1, U3.5 (VOUT), U4.4 (SD), U4.5 (V+), U5.1 (IN), U5.3 (EN); also elsewhere on the board
VDDA: C35.1, C36.1, U5.5 (OUT); also elsewhere on the board
VSSA: C37.1, C38.1, U6.5 (VOUT); also elsewhere on the board

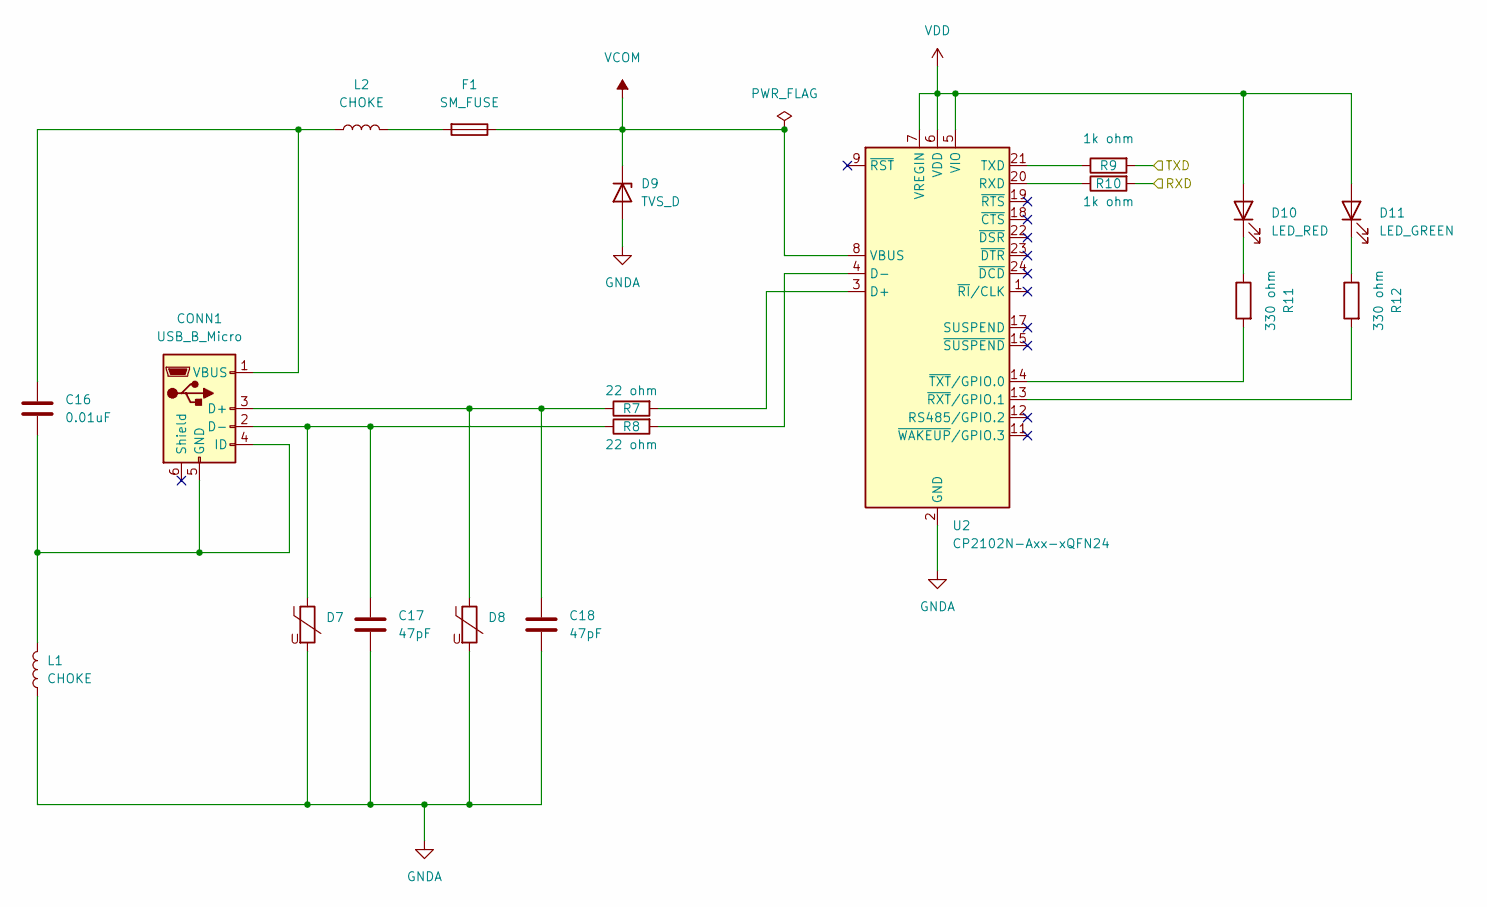
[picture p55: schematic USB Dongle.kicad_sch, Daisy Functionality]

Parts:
C16: 0.01uF; C_0402_1005Metric
C17, C18: 47pF; C_0402_1005Metric
CONN1: USB_B_Micro; USB_Micro-B_Molex-105017-0001
D7, D8: ESD_VARISTOR; D_0402_1005Metric
D9: TVS_D; ESDALC6V1-1M2
D10: LED_RED; LED_0603_1608Metric
D11: LED_GREEN; LED_0603_1608Metric
F1: SM_FUSE; Fuse_1812_4532Metric
L1, L2: CHOKE; L_0402_1005Metric
R7, R8: 22 ohm; R_0402_1005Metric
R9, R10: 1k ohm; R_0402_1005Metric
R11, R12: 330 ohm; R_0402_1005Metric
U2: CP2102N-Axx-xQFN24; QFN-24-1EP_4x4mm_P0.5mm_EP2.6x2.6mm

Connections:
/FROM_PC: R9.2; also elsewhere on the board
/TO_PC: R10.2; also elsewhere on the board
GNDA: C17.2, C18.2, D7.2, D8.2, D9.2 (A), L1.2, U2.2 (GND), U2.25 (GND); also elsewhere on the board
unnamed: C18.1, CONN1.3 (D+), D8.1, R7.1
unnamed: C17.1, CONN1.2 (D-), D7.1, R8.1
unnamed: C16.2, CONN1.4 (ID), CONN1.5 (GND), L1.1
unnamed: C16.1, CONN1.1 (VBUS), L2.2
unnamed: D10.1 (K), R11.1
unnamed: D11.1 (K), R12.1
unnamed: F1.2, L2.1
unnamed: R7.2, U2.3 (D+)
unnamed: R8.2, U2.4 (D-)
unnamed: R10.1, U2.20 (RXD)
unnamed: R9.1, U2.21 (TXD)
unnamed: R12.2, U2.13 (~RXT/GPIO.1)
unnamed: R11.2, U2.14 (~TXT/GPIO.0)
VCOM: D9.1 (K), F1.1, U2.8 (VBUS); also elsewhere on the board
VDD: D10.2 (A), D11.2 (A), U2.5 (VIO), U2.6 (VDD), U2.7 (VREGIN); also elsewhere on the board

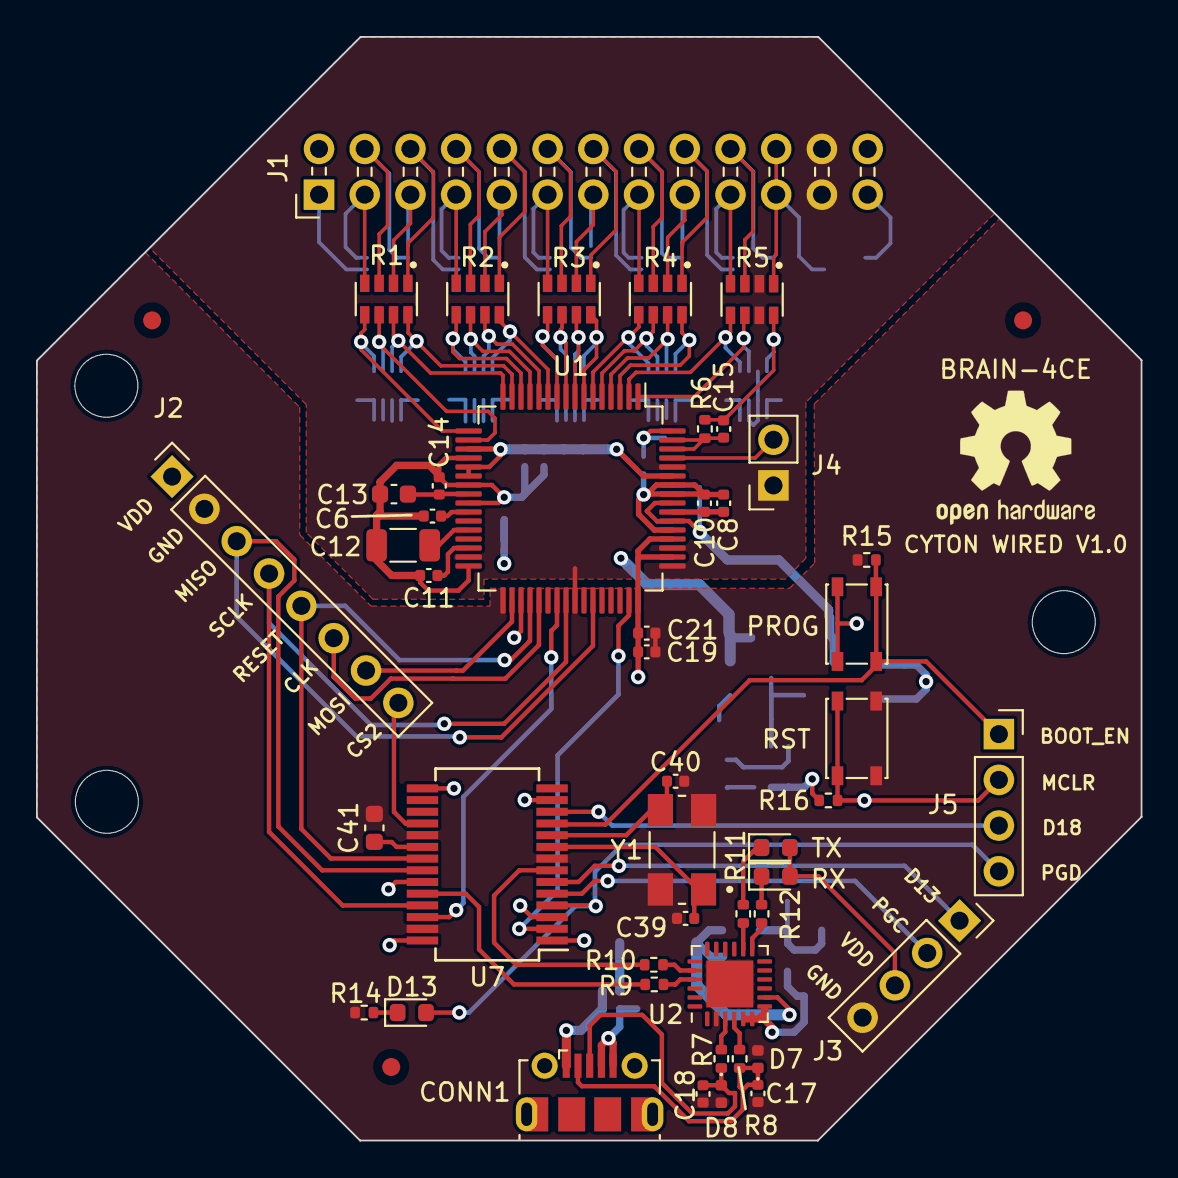
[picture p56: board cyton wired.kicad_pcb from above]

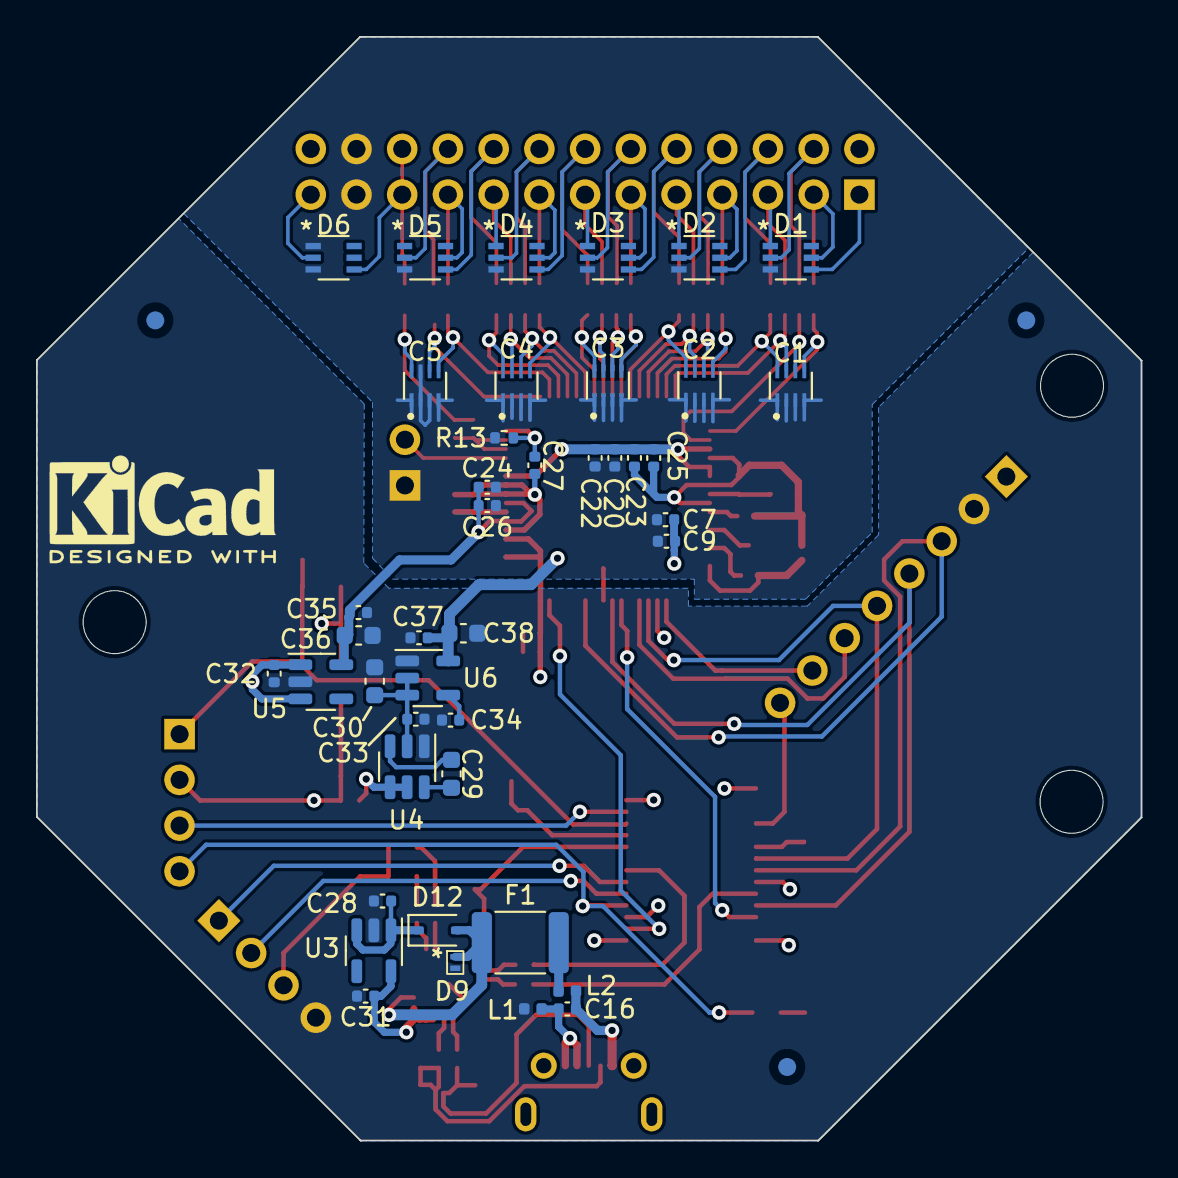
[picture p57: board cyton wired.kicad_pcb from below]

Board: 4 copper layers, 61.4 x 61.3 mm, 89 parts (42 on the bottom side), 89 nets.

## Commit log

2022-12-07 control camera pos on 'a'
2023-01-09 project snapshot
    [Daisy Functionality.kicad_sch, USB Dongle.kicad_sch, cyton hat.kicad_pcb, cyton hat.kicad_sch]
2023-01-10 finished layout
    [Daisy Functionality.kicad_sch, cyton hat-B_Cu.gbr, cyton hat-B_Mask.gbr, cyton hat-B_Paste.gbr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]
2023-01-11 moved via that missed VSSA plane
    [Daisy Functionality.kicad_sch, cyton hat-B_Cu.gbr, cyton hat-B_Mask.gbr, cyton hat-B_Paste.gbr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]
2023-01-12 fixed D9 footprint problem
    [Daisy Functionality.kicad_sch, USB Dongle.kicad_sch, cyton hat.kicad_pcb, cyton hat.kicad_sch]
2023-01-22 updated gerbers
    [cyton hat-B_Cu.gbr, cyton hat-B_Mask.gbr, cyton hat-B_Paste.gbr, cyton hat-B_Silkscreen.gbr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]
2023-01-24 GANTT CHART
    [GANTT CHART.xlsx]
2023-02-01 tentative camera angle changes
2023-02-17 sphObject now goes opposite direction of camera
2023-02-17 CAMERA ORIENTATION FIXED!
2023-03-04 restructured hardware files
    [Daisy Functionality.kicad_sch, USB Dongle.kicad_sch, cyton hat-B_Cu.gbr, cyton hat-B_Mask.gbr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]
2023-03-04 Added HW support for ADS129X
    [Daisy Functionality.kicad_sch, Power Supply.kicad_sch, USB Dongle.kicad_sch, cyton wired.kicad_pcb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]
2023-03-04 added power supply
    [Daisy Functionality.kicad_sch, Power Supply.kicad_sch, cyton wired.kicad_sch]
2023-03-05 snapshot of current MCU work
    [MCU.kicad_sch, cyton wired.kicad_sch]
2023-03-06 finished layout working on silkscreen
    [Daisy Functionality.kicad_sch, MCU.kicad_sch, Power Supply.kicad_sch, USB Dongle.kicad_sch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]
2023-03-06 fixed silk and generated fab outputs
    [cyton wired-B_Cu.gbr, cyton wired-B_Mask.gbr, cyton wired-B_Paste.gbr, cyton wired-B_Silkscreen.gbr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]
2023-03-06 renamed ADC schmatic for generatlity
    [ADS129X-X functionality.kicad_sch, cyton wired.kicad_sch]
2023-03-06 daisy design that support new ADC
    [ADS129X-X functionality.kicad_sch, cyton daisy-B_Cu.gbr, cyton daisy-B_Mask.gbr, cyton daisy-B_Paste.gbr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]
2023-03-07 changed C27 from an 0402 package to a 0201 package
    [ADS129X-X functionality.kicad_sch, Daisy Functionality.kicad_sch, MCU.kicad_sch, Power Supply.kicad_sch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]
2023-03-25 fixed RX and TX pins configuration
    [cyton wired.kicad_pcb, cyton wired.kicad_sch]
2023-03-25 added RX and TX silkscreen
    [cyton wired-B_Cu.gbr, cyton wired-B_Mask.gbr, cyton wired-B_Paste.gbr, cyton wired-B_Silkscreen.gbr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]
2023-03-27 enlarged mounting holes
    [cyton wired-B_Cu.gbr, cyton wired-B_Mask.gbr, cyton wired-B_Paste.gbr, cyton wired-B_Silkscreen.gbr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]
2023-03-27 removed silk from mounting holes
    [cyton wired-B_Cu.gbr, cyton wired-B_Mask.gbr, cyton wired-B_Paste.gbr, cyton wired-B_Silkscreen.gbr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]
2023-03-27 restructured hardware folder and added OpenBCI_GUI patch/documentation
    [ADS129X-X functionality.kicad_sch, Daisy Functionality.kicad_sch, MCU.kicad_sch, Power Supply.kicad_sch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]
2023-04-01 add brainflow code
    [out.csv]
2023-04-01 add stl and CAD drawings
    [CaseCover_V2.stl, Case_Drawings.dwg, CytonWired_CaseV1.stl, CytonWired_CaseV2.stl]
2023-04-02 current snapshot
2023-04-05 Remove 0 index
    [Channels_Ranked.csv]
2023-04-05 add fake ML
    [CaseCover_V2.stl, Case_Drawings.dwg, CytonWired_CaseV2.stl]
2023-04-11 add caseV3.stl
    [Case_V3.stl, Clip_wElectrode.stl, Cover_V3.stl]
2023-04-20 update hardware
    [Cover_V3.stl, Frame.stl]
2023-04-24 network architecture and dataloader
    [Case_Drawings.dwg]
2023-04-25 implement filter transform, begin trainer
2023-04-25 updated game flow logic
2023-04-28 add boardstreamer functionality
2023-04-30 add trained models + results
    [results.csv]
2023-05-01 Adding Hardware Report
    [cyton daisy bom.csv, cyton wired bom.csv]
2023-05-01 Adding prototype testing plans and reports
2023-05-03 change model, add new results
    [results.csv]
2023-05-04 rm models and results
    [results.csv]

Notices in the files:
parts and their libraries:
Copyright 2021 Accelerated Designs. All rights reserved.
